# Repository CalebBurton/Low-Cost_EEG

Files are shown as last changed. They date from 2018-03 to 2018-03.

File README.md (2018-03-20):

# Low-Cost EEG
___Repo for storing files related to the Low-Cost EEG project at Stellenbosch University during the 2018 Global Health Technologies exchange with Northwestern University.___

---

Hardware is modified from the [OpenBCI Ganglion](https://github.com/OpenBCI/Ganglion_Hardware_Design_Files), firmware is copied directly from the [Ganglion library](https://github.com/OpenBCI/OpenBCI_Ganglion_Library) with no modification.

All design files were made with [KiCad](http://kicad-pcb.org/) EDA software.

Tested with Arduino IDE v1.8.5, utilizing Simblee library v1.1.4 from [https://www.simblee.com/package_simblee166_index.json](https://www.simblee.com/package_simblee166_index.json). See [this page](https://www.simblee.com/support.html) for instructions on adding an external board to your board manager.

Programmed using an [FTDI cable](https://www.adafruit.com/product/70). FTDI drivers are not yet supported on macOS versions 10.11.0 and above, so programming was done in a Windows 10 virtual machine.

The OpenBCI GUI, used for visualizing and analyzing the output data, can be downloaded from [OpenBCI's downloads page](http://openbci.com/index.php/downloads). OpenBCI also provides documentation for the [Ganglion](http://docs.openbci.com/Tutorials/02-Ganglion_Getting%20Started_Guide) and the [GUI](http://docs.openbci.com/OpenBCI%20Software/01-OpenBCI_GUI).

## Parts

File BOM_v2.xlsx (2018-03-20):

Item | Reference | Value | Footprint | Description | Digikey Part No. | Link to Digikey Page | Qty | Cost (Each) | Cost (Total)
1 | C1, C11 | 22 µF | Through Hole | Capacitor 22uF | (Generic component) | (Generic component) | 2 | $0.00 | $0.00
2 | C2, C3, C4, C5, C12, C15, C18, C21, C24, C25, C29, C32 | 0.1 µF | Through Hole | Capacitor 0.1uF | (Generic component) | (Generic component) | 12 | $0.00 | $0.00
3 | C6, C8, C9, C10, C13, C14, C20, C23, C26, C28, C34 | 1 µF | Through Hole | Capacitor 1uF | (Generic component) | (Generic component) | 11 | $0.00 | $0.00
4 | C7 | 0.01 µF | Through Hole | Capacitor 0.01uF | (Generic component) | (Generic component) | 1 | $0.00 | $0.00
5 | C16, C17 | 18 pF | Through Hole | Capacitor 18pF | (Generic component) | (Generic component) | 2 | $0.00 | $0.00
6 | C19 | 47 µF | Through Hole | Capacitor 47uF | (Generic component) | (Generic component) | 1 | $0.00 | $0.00
7 | C22, C27, C36 | 10 µF | Through Hole | Capacitor 10uF | (Generic component) | (Generic component) | 3 | $0.00 | $0.00
8 | R1, R2, R3, R17 | 330 kΩ | Through Hole | Resistor 330k | (Generic component) | (Generic component) | 4 | $0.00 | $0.00
9 | R4, R9, R13, R14, R22, R27 | 1 MΩ | Through Hole | Resistor 1M | (Generic component) | (Generic component) | 6 | $0.00 | $0.00
10 | R5 | 100 Ω | Through Hole | Resistor 100 | (Generic component) | (Generic component) | 1 | $0.00 | $0.00
11 | R6, R7, R12, R23, R24, R25, R28, R29 | 100 kΩ | Through Hole | Resistor 100k | (Generic component) | (Generic component) | 8 | $0.00 | $0.00
12 | R8, R26 | 500 kΩ | Through Hole | Resistor 500k | (Generic component) | (Generic component) | 2 | $0.00 | $0.00
13 | R10, R11, R18, R19, R31 | 1 kΩ | Through Hole | Resistor 1k | (Generic component) | (Generic component) | 5 | $0.00 | $0.00
14 | R20, R21 | 5 kΩ | Through Hole | Resistor 5k | (Generic component) | (Generic component) | 2 | $0.00 | $0.00
15 | R30 | 10 kΩ | Through Hole | Resistor 10k | (Generic component) | (Generic component) | 1 | $0.00 | $0.00
16 | B1 (a) | 3.7V | - | 24.5mm Coin Battery | 1572-1621-ND | https://www.digikey.com/product-detail/en/illinois-capacitor/RJD2450/1572-1621-ND/6159139 | 1 | $3.82 | $3.82
17 | B1 (b) | - | 1053 | LIR2450 Battery Holder | 36-1053-ND | https://www.digikey.com/product-detail/en/keystone-electronics/1053/36-1053-ND/2745672 | 1 | $1.79 | $1.79
18 | D1 | - | Through Hole | Schottky diode | 497-2492-1-ND | https://www.digikey.com/product-detail/en/stmicroelectronics/BAT43/497-2492-1-ND/603874 | 1 | $0.47 | $0.47
19 | D2 | Blue | Through Hole | Power indicator LED | 754-1914-ND | https://www.digikey.com/product-detail/en/kingbright/WP710A10LVBC-D/754-1914-ND/5177415 | 1 | $0.56 | $0.56
20 | D3, D4, D5, D6, D7, D8, D9, D10, D11, D12 | - | Through Hole | 6V Zener diodes (input protection) | 1N5234BFSCT-ND | https://www.digikey.com/product-detail/en/on-semiconductor/1N5234BTR/1N5234BFSCT-ND/3504334 | 10 | $0.12 | $1.21
21 | SW1 | SPST (NO) | Through Hole | Tactile switch (reset button) | P8082SCT-ND | https://www.digikey.com/product-detail/en/panasonic-electronic-components/EVQ-11U04M/P8082SCT-ND/259567 | 1 | $0.23 | $0.23
22 | SW2 | SPDT | 3-pin SIP | Toggle switch (power switch) | EG1903-ND | https://www.digikey.com/product-detail/en/e-switch/EG1218/EG1903-ND/101726 | 1 | $0.58 | $0.58
23 | U1 | - | 8-pin DIP | 12-bit DAC (for Z test) | MCP4921-E/P-ND | https://www.digikey.com/product-detail/en/microchip-technology/MCP4921-E-P/MCP4921-E-P-ND/716280 | 1 | $2.09 | $2.09
24 | U2 | - | 8-pin DIP | Op Amp | 296-34316-5-ND | https://www.digikey.com/product-detail/en/texas-instruments/TL972IP/296-34316-5-ND/1906129 | 1 | $0.84 | $0.84
25 | U3, U8, U9 | - | 8-pin DIP | Op Amp | TC7650CPA-ND | https://www.digikey.com/product-detail/en/microchip-technology/TC7650CPA/TC7650CPA-ND/115291 | 3 | $3.61 | $10.83
26 | U4 | - | 8-pin DIP | 2-input NAND gates (2 per package) | 296-3504-5-ND | https://www.digikey.com/product-detail/en/texas-instruments/CD40107BE/296-3504-5-ND/376603 | 1 | $0.54 | $0.54
27 | U5, U6 | - | 8-pin DIP | Instrumentation Amp | AD627ANZ-ND | https://www.digikey.com/product-detail/en/analog-devices-inc/AD627ANZ/AD627ANZ-ND/750980 | 2 | $8.53 | $17.06
28 | U7 | - | 8-pin DIP | Op Amp | LTC1152CN8#PBF-ND | https://www.digikey.com/product-detail/en/linear-technology-analog-devices/LTC1152CN8-PBF/LTC1152CN8-PBF-ND/891149 | 1 | $6.15 | $6.15
29 | U10 | - | 8-pin DIP | Op Amp | MCP6002-I/P-ND | https://www.digikey.com/product-detail/en/microchip-technology/MCP6002-I-P/MCP6002-I-P-ND/500875 | 1 | $0.35 | $0.35
30 | U11 (a) | - | 28-pin SSOP | 4-channel ADC | MCP3912A1-E/SS-ND | https://www.digikey.com/product-detail/en/microchip-technology/MCP3912A1-E-SS/MCP3912A1-E-SS-ND/4079839 | 1 | $3.42 | $3.42
31 | U11 (b) | - | 28-pin DIP breakout | SSOP Breakout board | PA0020-ND | https://www.digikey.com/product-detail/en/chip-quik-inc/PA0020/PA0020-ND/5014752 | 1 | $5.79 | $5.79
32 | U14, U15, U16 | - | 8-pin DIP | Electric switches (for Z tests) | 296-21908-5-ND | https://www.digikey.com/product-detail/en/texas-instruments/TS12A4514P/296-21908-5-ND/1629081 | 3 | $0.76 | $2.28
33 | U17 | - | 7-pin SIP breakout | Micro SD card holder | 1568-1345-ND | https://www.digikey.com/product-detail/en/sparkfun-electronics/BOB-00544/1568-1345-ND/5824094 | 1 | $3.95 | $3.95
34 | U18, U21 | 3V | 8-pin DIP | Llinear voltage regulators | 296-1965-5-ND | https://www.digikey.com/product-detail/en/texas-instruments/TPS7230QP/296-1965-5-ND | 2 | $2.01 | $4.02
35 | U19 | - | 34-pin (16/18) DIP breakout | Simblee BLE/MCU dev board | 1568-1353-ND | https://www.digikey.com/product-detail/en/sparkfun-electronics/WRL-13632/1568-1353-ND/5870446 | 1 | $24.95 | $24.95
36 | U20 | - | 8-pin DIP | Voltage detector (for clean reset) | 296-11547-5-ND | https://www.digikey.com/product-detail/en/texas-instruments/UCC3946N/296-11547-5-ND/381725 | 1 | $3.76 | $3.76
37 | Y1 | 3.2768 MHz | HC49/U | Crystal oscillator | X980-ND | https://www.digikey.com/product-detail/en/ecs-inc/ECS-32-17-1X/X980-ND/827472 | 1 | $0.60 | $0.60
 |  |  |  |  |  |  |  |  | $95.29

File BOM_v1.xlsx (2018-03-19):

Item | Reference | Value | Thing | Part Number | Manufacturer | Footprint | QTY
1 | B1 | JS_2_Battery | Battery Connector | S2B-PH-SM4-TB(LF)(SN) | Various | OpenBCI:JST_RA_SMT | 1
2 | C10,C11,C12,C13,C25,C30,C33,C28,C19,C17,C23,C14,C45,C42,C40 | 1uF | C_0603 | GRM188R61E105KA12D | Murata | Capacitors_SMD:C_0603 | 15
3 | C34,C29,C18,C41 | 10uF | C_0603 | GRM188C80G106ME47D | Murata | Capacitors_SMD:C_0603 | 4
4 | C35 | 47uF | 47uF | GRM21BR60J476ME15L | Murata | Capacitors_SMD:C_1210 | 1
5 | C36 | 0.01uF | C_0603 | GCM188R71H103KA37D | Murata | Capacitors_SMD:C_0603 | 1
6 | C43,C38 | 18pF | C_0603 | GRM1885C1H180JA01D | Murata | Capacitors_SMD:C_0603 | 2
7 | C7,C5,C4,C2,C1,C3,C6,C8,C21,C24,C26,C31,C32,C27,C20,C15,C16,C22,C46 | 0.1uF | C_0603 | GRM188R71H104KA93D | Murata | Capacitors_SMD:C_0603 | 19
8 | C9,C37,C39,C44 | 22uF | C_0603 | GRM188R60J226MEA0D | Murata | Capacitors_SMD:C_0603 | 4
9 | D1 | D_Schottky | Schottkey Diode | CDBU0130L | Comchip | Capacitors_SMD:C_0603 | 1
10 | D2 | LED | Blue LED | LTST-C193TBKT-5A | Lite-On | LEDs:LED_0603 | 1
11 | P1 | CONN_02X08 | 2x8 RA Header Row | PRPC008DBAN-M71RC | Sullins | Pin_Headers:Pin_Header_Angled_2x08 | 1
12 | P2,P3 | CONN_01X04 | Socket_Strip_Straight_1x04 0.1” pitch | PPTC041LFBN-RC | Sullins | Socket_Strips:Socket_Strip_Straight_1x04 | 2
13 | P4,P5 | CONN_01X08 | Socket_Strip_Straight_1x08 0.1” pitch | PPTC081LFBN-RC | Sullins | Socket_Strips:Socket_Strip_Straight_1x08 | 2
14 | R16,R18,R20,R22 | 2K | R_0603 | ERJ-3EKF2001V | Panasonic | Resistors_SMD:R_0603 | 4
15 | R2,R3,R4,R5,R6,R7,R8,R9,R11,R49 | 330K | R_0603 | ERJ-3EKF3303V | Panasonic | Resistors_SMD:R_0603 | 10
16 | R23,R24,R25,R26,R47,R40,R41 | 1K | R_0603 | ERJ-3EKF1001V | Panasonic | Resistors_SMD:R_0603 | 7
17 | R34,R35,R48,R36 | 500K | R_0603 | CR0603-FX-4993ELF | Bourns | Capacitors_SMD:C_0603 | 4
18 | R37,R15,R17,R19,R21,R27,R28,R32,R33,R44,R45,R46 | 100K | R_0603 | ERJ-3EKF1003V | Panasonic | Resistors_SMD:R_0603 | 12
19 | R38 | 10K | Resistors_SMD: | ERJ-3EKF1002V | Panasonic | Resistors_SMD:R_0603 | 1
20 | R39 | 100R | 100R | ERJ-3EKF1000V | Panasonic | Resistors_SMD:R_0603 | 1
21 | R42,R43,R1,R12,R10,R13,R14,R30,R31,R29 | 1M | R_0603 | ERJ-3EKF1004V | Panasonic | Resistors_SMD:R_0603 | 10
22 | SW3,SW2,SW1,SW4 | CJS1200 | DIP Switch | CJS-1200TA | Copal | OpenBCI:CJS-1200TA | 4
23 | SW5 | SPDT | SPDT Power Switch | SSSS810701 | Alps | OpenBCI:SSSS810701 | 1
24 | SW6 | TACT_SWITCH | Tact Switch | PTS810 SJK 250 SMTR LFS | C&K | OpenBCI:PTS810 | 1
25 | U10 | NCP300 | Voltage Trigger | NCP300LSN30T1G | On Semi | TO_SOT_Packages_SMD:SOT-23-5 | 1
26 | U12 | AD5621 | 12bit DAC | AD5621AKSZ-REEL7 | Analog Devices | TO_SOT_Packages_SMD:SC-70-6 | 1
27 | U13 | SEEED_microSD | microSD Card | ST-TF-003A | SEEED | OpenBCI:ST-TF-0003A | 1
28 | U14 | MCP6V13T | OpAmp | MCP6V31T-E/OT | Microchip | TO_SOT_Packages_SMD:SOT-23-5 | 1
29 | U15 | MCP6001 | OpAmp | MCP6001T-I/LT | Microchip | TO_SOT_Packages_SMD:SC-70-5 | 1
30 | U16 | SN74LVC1G32 | NOR Gate | SN74LVC1G32DCKR | Texas Instrument | TO_SOT_Packages_SMD:SC-70-5 | 1
31 | U17 | LIS2DE12 | Accelerometer | LIS2DE12TR | ST Microelectronics | OpenBCI:LIS2DH12 | 1
32 | U2,U3,U4,U5 | AD8237 | InAmp | AD8237ARMZ-R7 | Analog Devices | Housings_SSOP:MSOP-8_3x3mm_Pitch0.65mm | 4
33 | U21,U19,U20,U18,U22 | 74LVC1G66 | Analog Switch IC | 74LVC1G66GW,125 | NXP | TO_SOT_Packages_SMD:SOT-353 | 5
34 | U23 | 74LVC2G00 | Dual NAND Gate | SN74LVC2G00DCUR | Texas Instrument | OpenBCI:VSSOP-8 | 1
35 | U25,U1,U24,U26,U27 | MCP6V31U | OpAmp | MCP6V31UT-E/LT | Texas Instrument | TO_SOT_Packages_SMD:SC-70-5 | 5
36 | U28,U30,U29 | TPD4E1B06 | TVS | TPD4E1B06DCKR | Texas Instrument | TO_SOT_Packages_SMD:SC-70-6 | 3
37 | U6 | LM7332 | Dual OpAmp | MCP6L02T-E/MS | Microchip | Housings_SSOP:MSOP-8_3x3mm_Pitch0.65mm | 1
38 | U7 | MCP3912 | AFE | MCP3912A1-E/SS | Microchip | Housings_SSOP:SSOP-28_5.3x10.2mm_Pitch0.65mm | 1
39 | U8 | rfd_77101 | Simblee | RFD-77101 | RF digital | OpenBCI:RFD77101 | 1
40 | U9,U11 | NCP551 | 3V Reg | NCP551SN30T1G | On Semi | TO_SOT_Packages_SMD:SOT-23-5 | 2
41 | Y1 | Xtal | 3.2768MHz | ABLS-LR-3.2768MHZ-T | Abracon | OpenBCI:ABM3C | 1

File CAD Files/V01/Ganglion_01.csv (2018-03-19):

Source: | /Users/calebburton/Documents/GitHub/Ganglion_Hardware_Design_Files/Ganglion_KiCad_Files/Ganglion_01.sch
Date: | Sunday, February 25, 2018 'PMt' 03:09:06 PM
Tool: | Eeschema 4.0.7
Component Count: | 99
Ref | Value | Footprint | Datasheet | Manufacturer | Vendor
B1 | JS_2_Battery | OpenBCI:JST_RA_SMT
C1 | 0.1uF | Capacitors_SMD:C_0603
C2 | 0.1uF | Capacitors_SMD:C_0603
C3 | 0.1uF | Capacitors_SMD:C_0603
C4 | 0.1uF | Capacitors_SMD:C_0603
C9 | 22uF | Capacitors_SMD:C_0603
C10 | 1uF | Capacitors_SMD:C_0603
C11 | 1uF | Capacitors_SMD:C_0603
C14 | 1uF | Capacitors_SMD:C_0603
C15 | 0.1uF | Capacitors_SMD:C_0603
C16 | 0.1uF | Capacitors_SMD:C_0603
C17 | 1uF | Capacitors_SMD:C_0603
C18 | 10uF | Capacitors_SMD:C_0603
C19 | 1uF | Capacitors_SMD:C_0603
C20 | 0.1uF | Capacitors_SMD:C_0603
C21 | 0.1uF | Capacitors_SMD:C_0603
C22 | 0.1uF | Capacitors_SMD:C_0603
C23 | 1uF | Capacitors_SMD:C_0603
C24 | 0.1uF | Capacitors_SMD:C_0603
C25 | 1uF | Capacitors_SMD:C_0603
C26 | 0.1uF | Capacitors_SMD:C_0603
C27 | 0.1uF | Capacitors_SMD:C_0603
C28 | 1uF | Capacitors_SMD:C_0603
C29 | 10uF | Capacitors_SMD:C_0603
C30 | 1uF | Capacitors_SMD:C_0603
C31 | 0.1uF | Capacitors_SMD:C_0603
C32 | 0.1uF | Capacitors_SMD:C_0603
C33 | 1uF | Capacitors_SMD:C_0603
C34 | 10uF | Capacitors_SMD:C_0603
C35 | 100uF | Capacitors_SMD:C_1210
C36 | 0.01uF | Capacitors_SMD:C_0603
C38 | 18pF | Capacitors_SMD:C_0603
C39 | 22uF | Capacitors_SMD:C_0603
C40 | 1uF | Capacitors_SMD:C_0603
C43 | 18pF | Capacitors_SMD:C_0603
C45 | 1uF | Capacitors_SMD:C_0603
C46 | 1uF | Capacitors_SMD:C_0603
D1 | D_Schottky | Capacitors_SMD:C_0603
D2 | LED | LEDs:LED_0603
P1 | CONN_02X08 | Pin_Headers:Pin_Header_Angled_2x08
P2 | CONN_01X04 | Socket_Strips:Socket_Strip_Straight_1x04
P3 | CONN_01X04 | Socket_Strips:Socket_Strip_Straight_1x04
P4 | CONN_01X08 | Socket_Strips:Socket_Strip_Straight_1x08
P5 | CONN_01X08 | Socket_Strips:Socket_Strip_Straight_1x08
R1 | 1M | Capacitors_SMD:C_0603
R2 | 330K | Resistors_SMD:R_0603
R4 | 330K | Resistors_SMD:R_0603
R11 | 330K | Resistors_SMD:R_0603
R12 | 1M | Capacitors_SMD:C_0603
R14 | 1M | Capacitors_SMD:C_0603
R15 | 100K | Resistors_SMD:R_0603
R16 | 2K | Resistors_SMD:R_0603
R17 | 100K | Resistors_SMD:R_0603
R18 | 2K | Resistors_SMD:R_0603
R23 | 1K | Resistors_SMD:R_0603
R24 | 1K | Resistors_SMD:R_0603
R27 | 100K | Resistors_SMD:R_0603
R28 | 100K | Resistors_SMD:R_0603
R30 | 1M | Capacitors_SMD:C_0603
R32 | 100K | Resistors_SMD:R_0603
R33 | 100K | Resistors_SMD:R_0603
R34 | 500K | Capacitors_SMD:C_0603
R36 | 500K | Capacitors_SMD:C_0603
R37 | 100K | Resistors_SMD:R_0603
R38 | 10K | Resistors_SMD:R_0603
R39 | 100 | Resistors_SMD:R_0603
R40 | 1K | Resistors_SMD:R_0603
R41 | 1K | Resistors_SMD:R_0603
R42 | 1M | Resistors_SMD:R_0603
R43 | 1M | Resistors_SMD:R_0603
R44 | 100K | Resistors_SMD:R_0603
R45 | 100K | Resistors_SMD:R_0603
R46 | 100K | Resistors_SMD:R_0603
R47 | 1K | Resistors_SMD:R_0603
R49 | 330K | Resistors_SMD:R_0603
SW5 | SPDT | OpenBCI:SSSS810701SSSS810701
SW6 | TACT_SWITCH | OpenBCI:PTS810
U1 | MCP6V31U | TO_SOT_Packages_SMD:SC-70-5
U2 | AD8237 | Housings_SSOP:MSOP-8_3x3mm_Pitch0.65mm
U3 | AD8237 | Housings_SSOP:MSOP-8_3x3mm_Pitch0.65mm
U6 | LM7332 | Housings_SSOP:MSOP-8_3x3mm_Pitch0.65mm
U7 | MCP3912 | Housings_SSOP:SSOP-28_5.3x10.2mm_Pitch0.65mm
U8 | rfd_77101 | OpenBCI:RFD77101
U9 | NCP551 | TO_SOT_Packages_SMD:SOT-23-5
U10 | NCP300 | TO_SOT_Packages_SMD:SOT-23-5
U11 | NCP551 | TO_SOT_Packages_SMD:SOT-23-5
U12 | AD5621 | TO_SOT_Packages_SMD:SC-70-6
U13 | SEEED_microSD | OpenBCI:ST-TF-0003A
U14 | MCP6V13T | TO_SOT_Packages_SMD:SOT-23-5
U15 | MCP6001 | TO_SOT_Packages_SMD:SC-70-5
U18 | 74LVC1G66 | TO_SOT_Packages_SMD:SC-70-5
U21 | 74LVC1G66 | TO_SOT_Packages_SMD:SC-70-5
U22 | 74LVC1G66 | TO_SOT_Packages_SMD:SC-70-5
U23 | 74LVC2G00 | OpenBCI:VSSOP-8
U25 | MCP6V31U | TO_SOT_Packages_SMD:SC-70-5
U26 | MCP6V31U | TO_SOT_Packages_SMD:SC-70-5
U28 | TPD4E1B06 | TO_SOT_Packages_SMD:SC-70-6
U29 | TPD4E1B06 | TO_SOT_Packages_SMD:SC-70-6
Y1 | Crystal_Small | Crystals:Crystal_HC49-SD_SMD

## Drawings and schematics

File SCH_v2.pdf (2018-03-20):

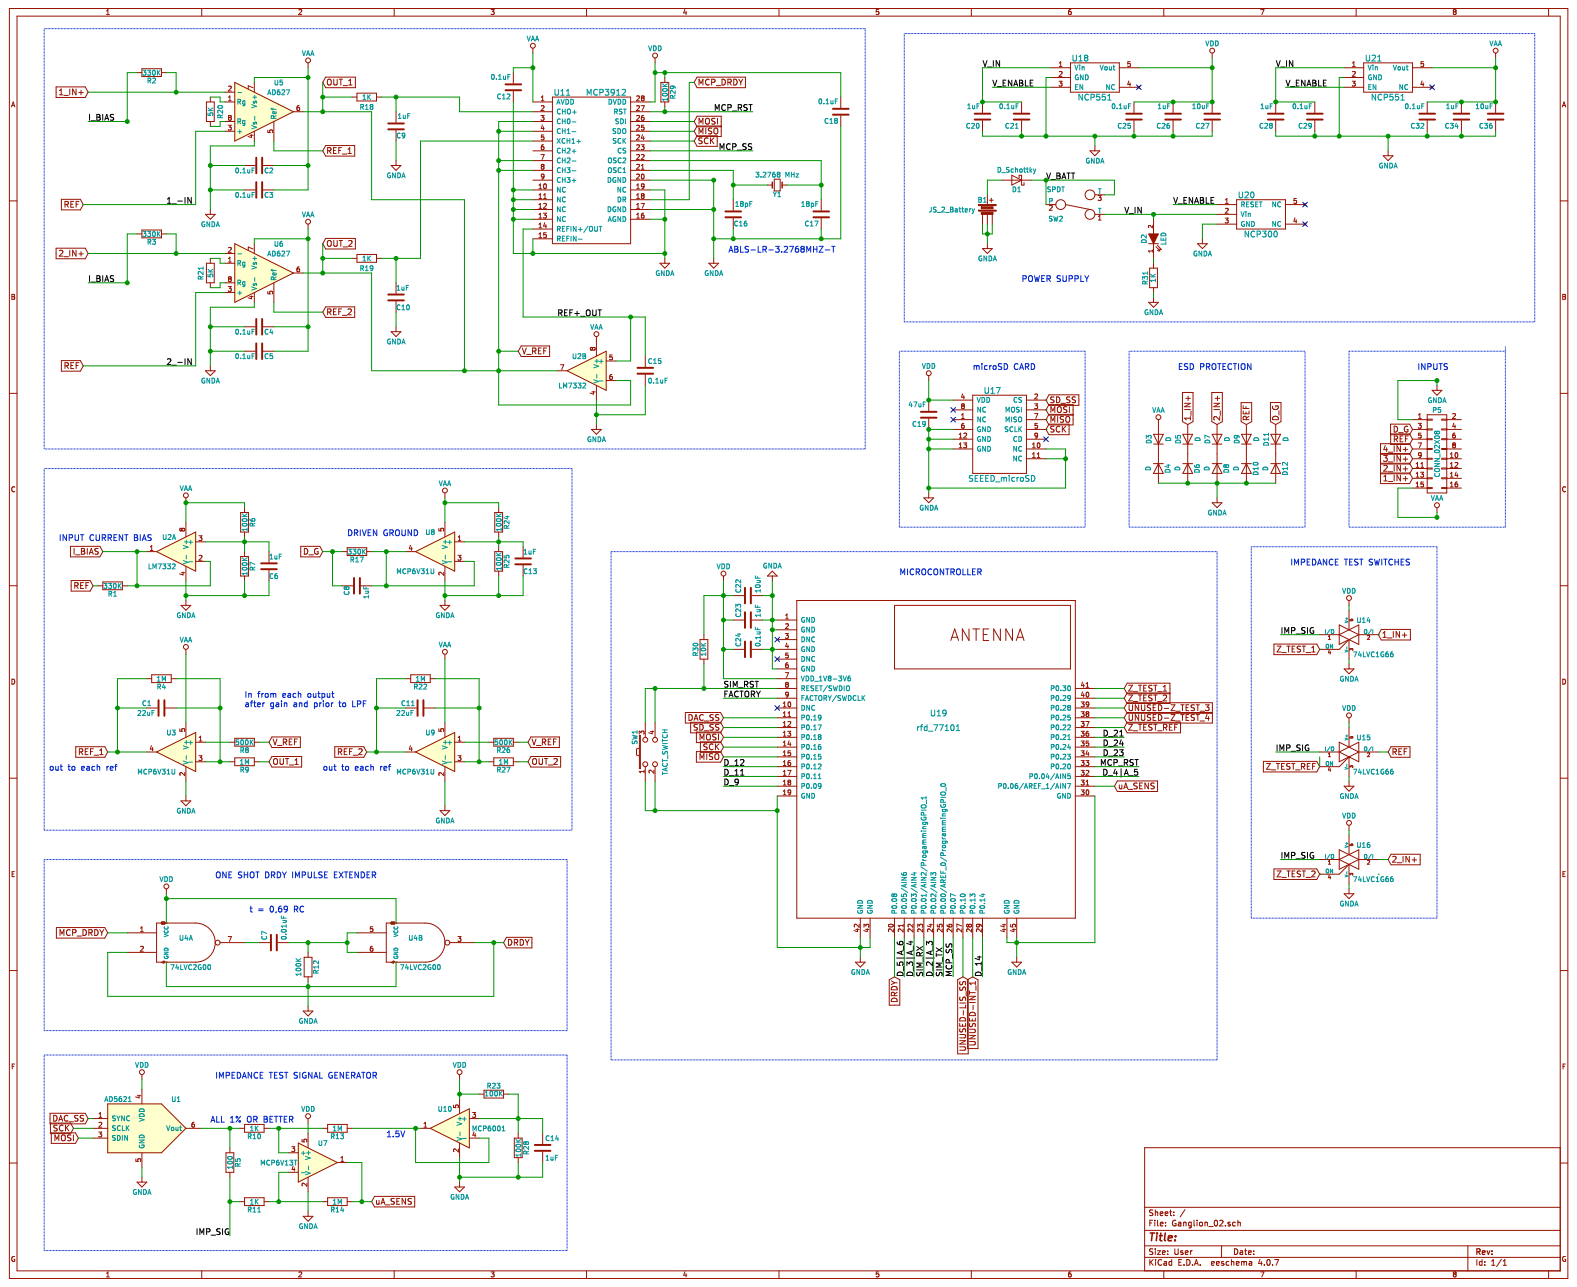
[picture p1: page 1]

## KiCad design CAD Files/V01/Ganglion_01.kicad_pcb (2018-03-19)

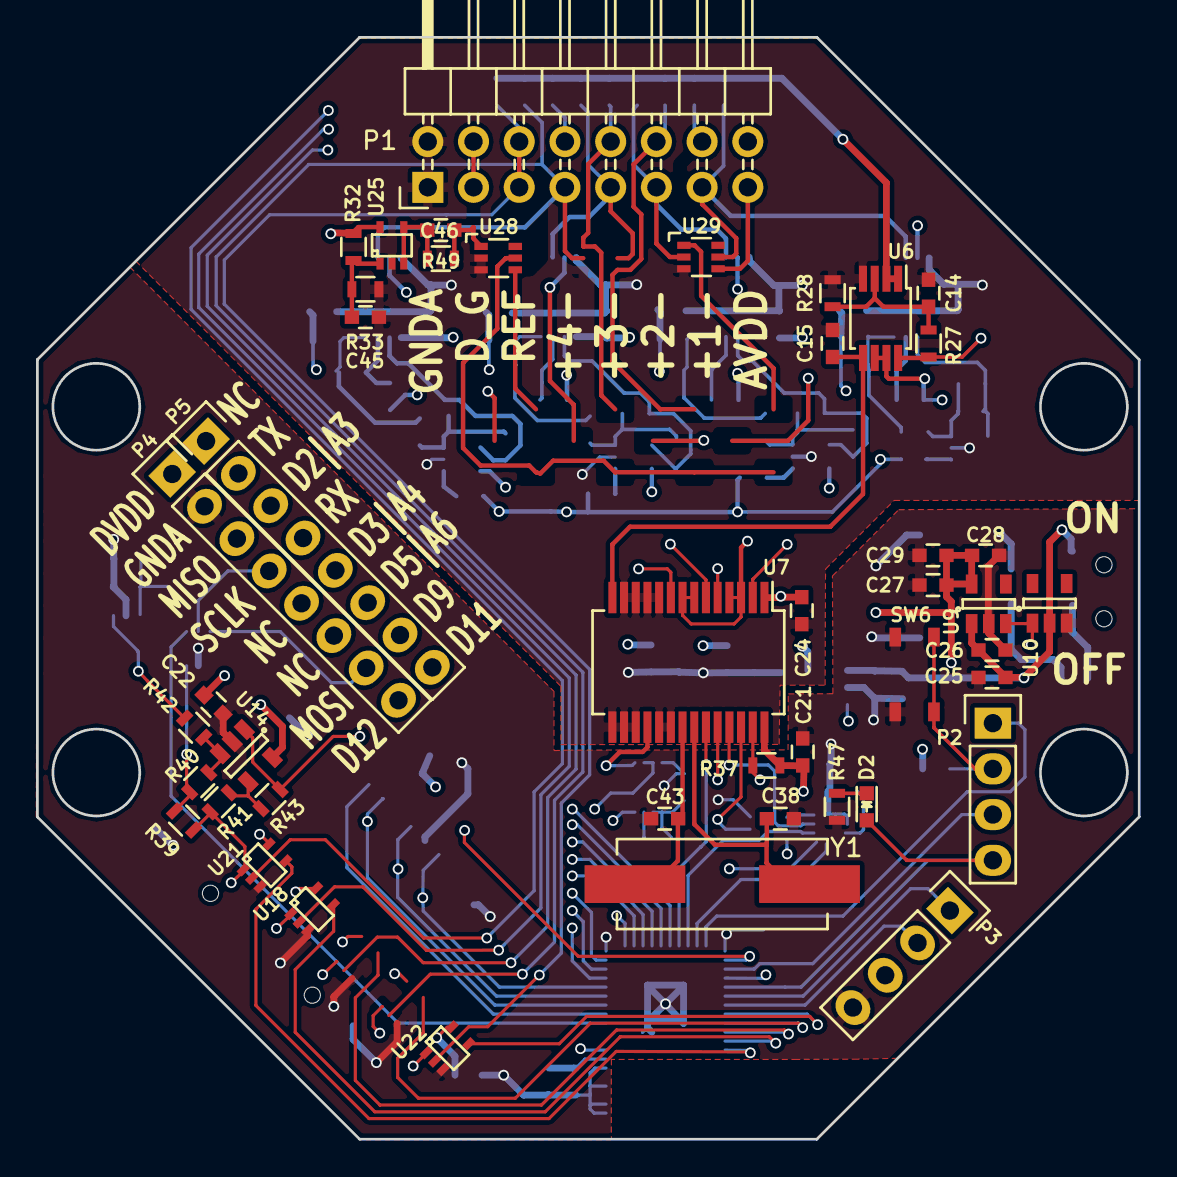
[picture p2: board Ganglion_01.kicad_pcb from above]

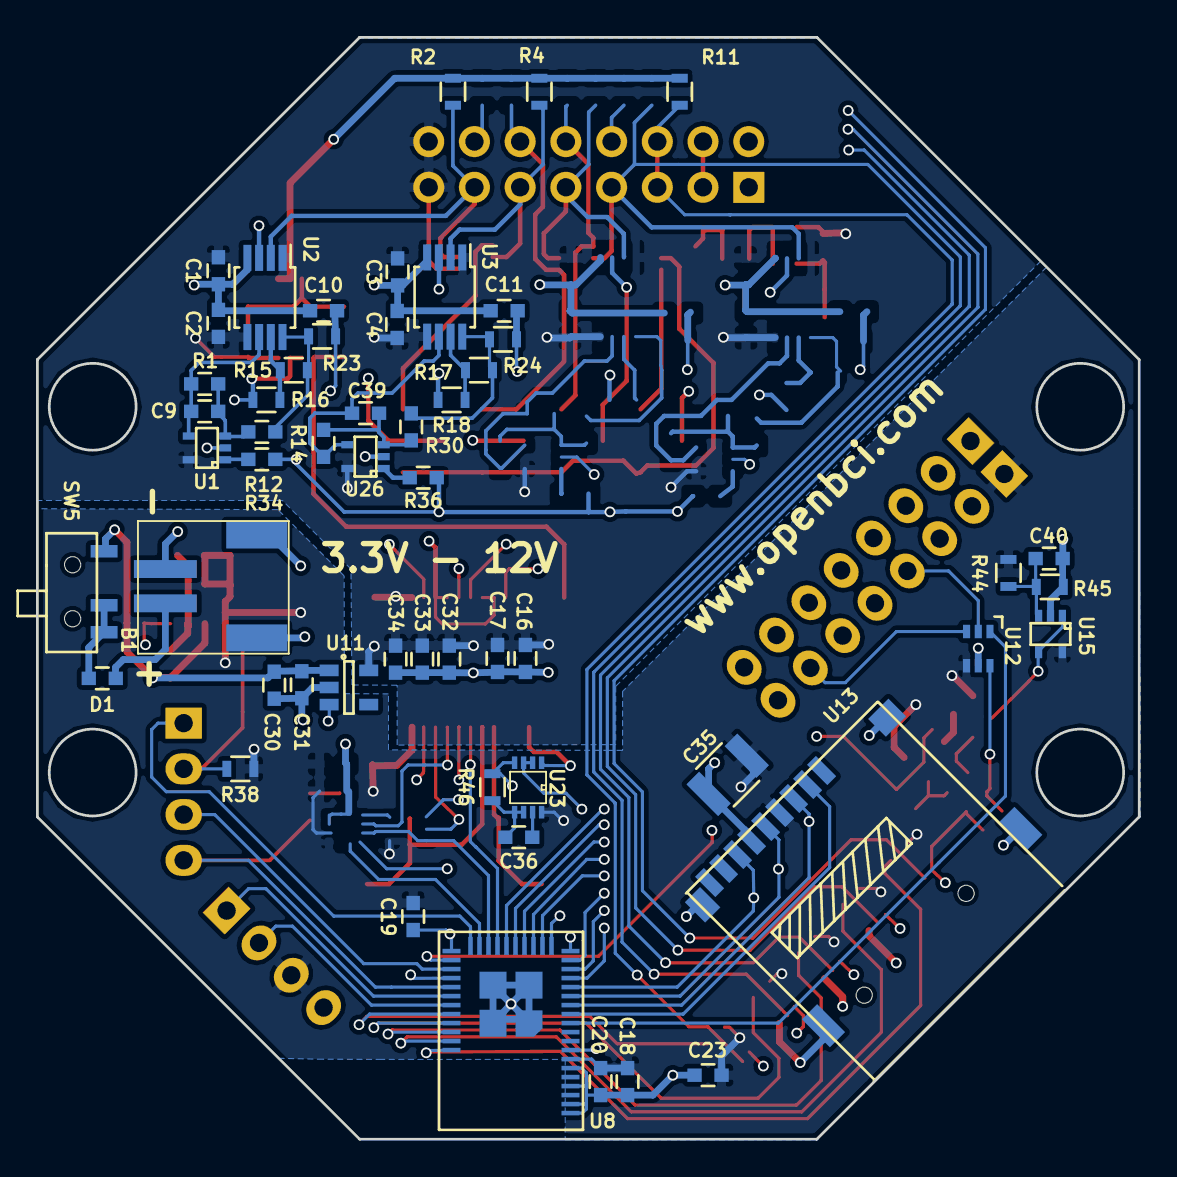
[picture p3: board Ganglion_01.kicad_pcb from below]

Board: 4 copper layers, 61.2 x 61.2 mm, 99 parts (54 on the bottom side), 67 nets.

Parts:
B1: JS_2_Battery; JST_RA_SMT
C1, C2, C3, C4, C15, C16, C20, C21, C22, C24, C26, C27, C31, C32: 0.1uF; C_0603
C9, C39: 22uF; C_0603
C10, C11, C14, C17, C19, C23, C25, C28, C30, C33, C40, C45, C46: 1uF; C_0603
C18, C29, C34: 10uF; C_0603
C35: 100uF; C_1210
C36: 0.01uF; C_0603
C38, C43: 18pF; C_0603
D1: D_Schottky; C_0603
D2: LED; LED_0603
P1: CONN_02X08; Pin_Header_Angled_2x08
P2, P3: CONN_01X04; Socket_Strip_Straight_1x04
P4, P5: CONN_01X08; Socket_Strip_Straight_1x08
R1, R12, R14, R30: 1M; C_0603
R2, R4, R11, R49: 330K; R_0603
R15, R17, R27, R28, R32, R33, R37, R44, R45, R46: 100K; R_0603
R16, R18: 2K; R_0603
R23, R24, R40, R41, R47: 1K; R_0603
R34, R36: 500K; C_0603
R38: 10K; R_0603
R39: 100; R_0603
R42, R43: 1M; R_0603
SW5: SPDT; SSSS810701SSSS810701
SW6: TACT_SWITCH; PTS810
U1, U25, U26: MCP6V31U; SC-70-5
U2, U3: AD8237; MSOP-8_3x3mm_Pitch0.65mm
U6: LM7332; MSOP-8_3x3mm_Pitch0.65mm
U7: MCP3912; SSOP-28_5.3x10.2mm_Pitch0.65mm
U8: rfd_77101; RFD77101
U9, U11: NCP551; SOT-23-5
U10: NCP300; SOT-23-5
U12: AD5621; SC-70-6
U13: SEEED_microSD; ST-TF-0003A
U14: MCP6V13T; SOT-23-5
U15: MCP6001; SC-70-5
U18, U21, U22: 74LVC1G66; SC-70-5
U23: 74LVC2G00; VSSOP-8
U28, U29: TPD4E1B06; SC-70-6
Y1: Crystal_Small; Crystal_HC49-SD_SMD

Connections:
1_IN+: P1.13, R2.1, U2.2, U21.2, U29.5
2_IN+: P1.11, R4.1, U3.2, U18.2, U29.2
/D_2|A_3: P5.3, U8.24
/D_3|A_4: P5.5, U8.22
/D_4|A_5: P2.3, U8.32
/D_5|A_6: P5.6, U8.21
/D_9: P5.7, U8.18
/D_11: P5.8, U8.17
/D_12: P4.8, U8.16
/D_14: P2.1, U8.29
/D_21: P3.2, U8.36
/D_23: D2.2, P2.4, U8.34
/D_24: P3.1, U8.35
/MCP_RST: R37.2, U7.27, U8.33
/MCP_SS: U7.23, U8.26
/REF+_OUT: C15.1, U6.5, U7.14
/SENSORS/IMP_SIG: R39.2, R41.2, U18.1, U21.1, U22.1
/SIM_RST: P2.2, R38.1, SW6.3, SW6.4, U8.8
/SIM_RX: P5.4, U8.23
/SIM_TX: P5.2, U8.25
/V_BATT: D1.1, SW5.2, SW5.3
/V_ENABLE: U9.3, U10.1, U11.3
/V_IN: C25.2, C26.2, C30.2, C31.2, SW5.1, U9.1, U10.2, U11.1
DAC_SS: U8.11, U12.1
DRDY: U8.20, U23.2, U23.3
D_G: C46.2, P1.3, R49.2, U28.1
GNDA: B1.2, B1.3, B1.4, C1.2, C2.2, C3.2, C4.2, C10.1, C11.2, C14.2, C15.2, C16.2, C17.2, C18.2, C19.2, C20.2, C21.1, C22.2, C23.2, C24.1, C25.1, C26.1, C27.1, C28.1, C29.1, C30.1, C31.1, C32.1, C33.1, C34.1, C35.1, C38.1, C40.2, C43.1, C45.2, P1.1, P3.4, P4.2, R28.2, R33.2, R45.2, R46.2, R47.2, SW6.1, SW6.2, U1.2, U2.4, U3.4, U6.4, U7.10, U7.11, U7.12, U7.13, U7.15, U7.16, U7.17, U7.19, U7.20, U8.1, U8.2, U8.4, U8.6, U8.19, U8.30, U8.42, U8.43, U8.44, U8.45, U9.2, U10.3, U11.2, U12.5, U13.6, U13.10, U13.11, U13.12, U13.13, U14.2, U15.2, U18.3, U21.3, U22.3, U23.4, U25.2, U26.2, U28.2, U28.3, U29.3
I_BIAS: R2.2, R4.2, R11.1, U6.1, U6.2
MCP_DRDY: U7.18, U23.1
MISO: P4.3, U7.25, U8.15, U13.7
MOSI: P4.7, U7.26, U8.13, U12.3, U13.3
unnamed: B1.1, D1.2
unnamed: C9.1, R1.1, R12.2, U1.3
unnamed: C10.2, R23.1, U7.2
unnamed: C11.1, R24.1, U7.5
unnamed: C14.1, R27.2, R28.1, U6.3
unnamed: C36.1, U23.7
unnamed: C36.2, R46.1, U23.5, U23.6
unnamed: C38.2, U7.22, Y1.1
unnamed: C39.1, R14.1, R30.2, U26.3
unnamed: C40.1, R44.2, R45.1, U15.3
unnamed: C43.2, U7.21, Y1.2
unnamed: C45.1, R32.2, R33.1, U25.1
unnamed: C46.1, R49.1, U25.3, U25.4
unnamed: D2.1, R47.1
unnamed: R15.1, R16.1, U2.7
unnamed: R17.1, R18.1, U3.7
unnamed: R34.2, U1.1
unnamed: R36.2, U26.1
unnamed: R39.1, R40.2, U12.6
unnamed: R40.1, R42.2, U14.3
unnamed: R41.1, R43.2, U14.4
unnamed: R42.1, U15.1, U15.4
OUT_1: R12.1, R15.2, R23.2, U2.8
OUT_2: R17.2, R24.2, R30.1, U3.8
REF: P1.5, R11.2, U2.3, U3.3, U22.2, U28.5
REF_1: C9.2, R1.2, U1.4, U2.6
REF_2: C39.2, R14.2, U3.6, U26.4
SCK: P4.4, U7.24, U8.14, U12.2, U13.5
SD_SS: U8.12, U13.2
VAA: C1.1, C2.1, C3.1, C4.1, C16.1, C17.1, C24.2, C32.2, C33.2, C34.2, P1.15, R27.1, R32.1, U1.5, U2.1, U2.5, U3.1, U3.5, U6.8, U7.1, U11.5, U25.5, U26.5, U29.4
VDD: C18.1, C19.1, C20.1, C21.2, C22.1, C23.1, C27.2, C28.2, C29.2, C35.2, P3.3, P4.1, R37.1, R38.2, R44.1, U7.28, U8.7, U9.5, U12.4, U13.4, U14.5, U15.5, U18.5, U21.5, U22.5, U23.8
V_REF: R16.2, R18.2, R34.1, R36.1, U6.6, U6.7, U7.3, U7.4, U7.7, U7.8
Z_TEST_1: U8.41, U21.4
Z_TEST_2: U8.40, U18.4
Z_TEST_REF: U8.37, U22.4
uA_SENS: R43.1, U8.31, U14.1

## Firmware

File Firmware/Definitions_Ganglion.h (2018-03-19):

//
//

#ifndef _Definitions_Ganglion_h
#define _Definitions_Ganglion_h

#define LED 23
#define LED_DELAY_TIME 300
#define RING_SIZE 101
#define SERIAL_BUFFER_LENGTH  20
#define MAX_BYTES_PER_PACKET  19

// Byte IDs
#define ID_RAW_DATA 0
#define ID_SAMPLE_18_MIN 1
#define ID_SAMPLE_18_MAX 100
#define ID_SAMPLE_19_MIN 101
#define ID_SAMPLE_19_MAX 200
#define ID_Z_1  201
#define ID_Z_2  202
#define ID_Z_3  203
#define ID_Z_4  204
#define ID_Z_R  205
#define ID_MULTI_PACKET 206
#define ID_MULTI_PACKET_STOP  207

// Serial Command Characters
#define DEACTIVATE_CHANNEL_1 '1'
#define DEACTIVATE_CHANNEL_2 '2'
#define DEACTIVATE_CHANNEL_3 '3'
#define DEACTIVATE_CHANNEL_4 '4'
#define ACTIVATE_CHANNEL_1 '!'
#define ACTIVATE_CHANNEL_2 '@'
#define ACTIVATE_CHANNEL_3 '#'
#define ACTIVATE_CHANNEL_4 '$'
#define START_DATA_STREAM 'b'
#define STOP_DATA_STREAM 's'
#define ENABLE_ACCELEROMETER 'n'
#define DISABLE_ACCELEROMETER 'N'
#define ENABLE_SYNTHETIC_DATA '['
#define DISABLE_SYNTHETIC_DATA ']'
#define SOFT_RESET 'v'
#define REPORT_REGISTER_SETTINGS '?'
#define ENABLE_OTA '>'
#define OPENBCI_SAMPLE_RATE_SET '~'

#define OPENBCI_CHANNEL_1 '1'
#define OPENBCI_CHANNEL_2 '2'
#define OPENBCI_CHANNEL_3 '3'
#define OPENBCI_CHANNEL_4 '4'
#define OPENBCI_CHANNEL_REF '5'

#define OPENBCI_Z_TEST_START 'z'
#define OPENBCI_Z_TEST_STOP 'Z'

//  MCP
#define DEACTIVATE 0
#define ACTIVATE 1
#define ENABLE_0   0x000E0000
#define ENABLE_1   0x000D0000
#define ENABLE_2   0x000B0000
#define ENABLE_3   0x00070000
#define DISABLE_0  0x00010000
#define DISABLE_1  0x00020000
#define DISABLE_2  0x00040000
#define DISABLE_3  0x00080000

#define MCP_SS  7   // MCP Slave Select on Simblee pin 13
#define MCP_DRDY 8   // MCP DataReady on Simblee pin 8
#define MCP_RST 20   // MCP Reset: active low

#define MCP_ADD  0x40
#define MCP_READ  0x01
#define MCP_WRITE  0x00

#define DEV_ADD  0x40

#define CHAN_0  0x00       //00   |        | -GROUP
#define CHAN_1  0x02       //01   |-TYPE  _|
#define CHAN_2  0x04       //02   |        | -GROUP
#define CHAN_3  0x06       //03  _|       _|

#define MOD_VAL  0x10      //08   |        |
#define PHASE  0x14        //0A   |        |-GROUP
#define GAIN  0x16         //0B   |       _|
#define STATUSCOM  0x18    //0C   |        |
#define CONFIG_0  0x1A     //0D   |        |-GROUP
#define CONFIG_1  0x1C     //0E   |       _|
#define OFFCAL_0  0x1E     //0F   |-TYPE   | -GROUP
#define GAINCAL_0  0x20    //10   |       _|
#define OFFCAL_1  0x22     //11   |        | -GROUP
#define GAINCAL_1  0x24    //12   |       _|
#define OFFCAL_2  0x26     //13   |        | -GROUP
#define GAINCAL_2  0x28    //14   |       _|
#define OFFCAL_3  0x2A     //15   |        | -GROUP
#define GAINCAL_3  0x2C    //16   |       _|
#define LOK_CRC  0x3E      //1F  _|        >-GROUP

#define GAIN_1  0x00000000
#define GAIN_2  0x00000249
#define GAIN_4  0x00000492
#define GAIN_8  0x000006CB
#define GAIN_16 0x00000924
#define GAIN_32 0x00000B6D

//  0x0038E050
// #define SAMPLE_25   0x00030000
// #define SAMPLE_50   0x00020000
// #define SAMPLE_100  0x00010000
// #define SAMPLE_200  0x00000000


//#define OPENBCI_NUMBER_OF_BYTES_SETTINGS_Z_TEST 3
#define HALF_PERIOD 3000
#define HALF_WAVE 100
#define SHUNT 100
#define SHUNT_SENSOR_GAIN 1000
#define UA_SAMPLE_TIME 500
#define UA_SAMPLE_LIMIT 1000


/*
 *  AD5621
 */
#define DAC_MASK  0x3FFC
#define SHUNT_SENSOR 6     // reads the current shunt sensor
#define DAC_SS    19       // DAC slave select
#define Z_TEST_1  30       // pin control for Z test channel 1
#define Z_TEST_2  29       // pin control for Z test channel 2
#define Z_TEST_3  28       // pin control for Z test channel 3
#define Z_TEST_4  25       // pin control for Z test channel 4
#define Z_TEST_REF  22     // pin control for Z test channel REF
// CONTROL BYTES
#define DAC_EN    0x0000  // enables setting the DAC output 12 bit resolution
#define DAC_1K    0x7000  // disables DAC with output tied 1K to GND
#define DAC_100K  0x8000  // disables DAC with output tied 100K to GND
#define DAC_Z     0xC000  // disables DAC with output in high Z
#define DAC_MAX   0xFFFF  // highest possible value of DAC = 4095




/*
 * LIS2DH
 */

#define LIS2DH_SS   10
#define LIS_DRDY    13

#define READ_REG    0x80
#define READ_MULTI    0x40

#define LIS3DH_MODE   3 // c pol =1, c pha = 1, mode = 3

#define STATUS_REG_AUX  0x07
#define OUT_TEMP_L      0x0C
#define OUT_TEMP_H      0x0D
#define INT_COUNTER_REG 0x0E
#define WHO_AM_I        0x0F
#define TEMP_CFG_REG    0x1F
#define CTRL_REG1       0x20
#define CTRL_REG2       0x21
#define CTRL_REG3       0x22
#define CTRL_REG4       0x23
#define CTRL_REG5       0x24
#define CTRL_REG6       0x25
#define REFERENCE       0x26
#define STATUS_REG2     0x27
#define OUT_X_L         0x28
#define OUT_X_H         0x29
#define OUT_Y_L         0x2A
#define OUT_Y_H         0x2B
#define OUT_Z_L         0x2C
#define OUT_Z_H         0x2D
#define FIFO_CTRL_REG   0x2E
#define FIFO_SRC_REG    0x2F
#define INT1_CFG        0x30
#define INT1_SOURCE     0x31
#define INT1_THS        0x32
#define INT1_DURATION   0x33
#define INT2_CFG        0x34
#define INT2_SOURCE     0x35
#define INT2_THS        0x36
#define INT2_DURATION   0x37
#define CLICK_CFG       0x38
#define CLICK_SRC       0x39
#define CLICK_THS       0x3A
#define TIME_LIMIT      0x3B
#define TIME_LATENCY    0x3C
#define TIME_WINDOW     0x3D
#define ACT_THS         0x3E
#define ACT_DUR         0x3F

/*
* SD CARD
*/
#define SD_SS 17

/** Wifi Stuff */
#define NUM_CHANNELS 4
#define OPENBCI_WIFI_ATTACH '{'
#define OPENBCI_WIFI_REMOVE '}'
#define OPENBCI_WIFI_STATUS ':'
#define OPENBCI_WIFI_RESET ';'

#endif

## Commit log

2018-03-19 Porting from fork of Ganglion repo
    [Ganglion_01.csv, Ganglion_01.kicad_pcb, Ganglion_01.sch, Ganglion_01_BOM.xlsx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]
2018-03-20 Update BOM
    [BOM_digikey.csv, BOM_v1.xlsx, BOM_v2.xlsx]
2018-03-20 Update BOM to match new schematic refs
    [BOM_digikey.csv, BOM_v2.xlsx, Ganglion_01.csv, Ganglion_01.kicad_pcb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]
2018-03-20 Update ESD protection block
    [BOM_v2.xlsx, Ganglion_02.sch]
2018-03-20 Fixed typo in BOM
    [BOM_v2.xlsx]
2018-03-20 Update instrumentation amps with DIP replacements
    [BOM_v2.xlsx, Ganglion_02.sch]
2018-03-20 Remove two unnecessary bypass capacitors
    [BOM_v2.xlsx]
